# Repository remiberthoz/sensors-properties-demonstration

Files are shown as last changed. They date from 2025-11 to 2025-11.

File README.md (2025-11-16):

# Simulated absorbance sensors

This program simulates a series of light intensity sensors based on a single
physical sensor. It is designed primarily for educational purposes to teach
biology or chemistry students about sensor properties. Simulated sensors have
different properties (linearity, sensitivity, range, response time, noise).
The program visualizes the behavior of these simulated sensors in real-time,
allowing for a hands-on, inexpensive way to discover these concepts.

## Problems to fix / todo list...

- The calibration procedure is not OK, it should somehow take the value of
  MAX_A into account ; and likely the complete scaling (with to_byte).

- Try to output sensor values on DAC such that the students can work on an
  oscilloscope. Check if the DAC communication rate is good enough to
  simulate real analog.

- Program Arduino IO to read jumper status, and potentially allow students to
  change easily configuration.

## TECHNICAL REQUIREMENTS

### Hardware

The program is designed to run on an Arduino Uno board (or compatible) fitted
whith a companion shield that holds a light source, a light sensor, and a
sample holder for spectrophotometry cuvettes.

The light source and the sensor are positioned approximately 1 cm apart,
separated by the cuvette holder, which is used to adjust light intensities on
the sensor.

Refer to the schematic for connections and for part numbers that I used (also
see below). The cuvette holder was 3d printed, the 3d model is available.

shield_schematic

shield_layout

shield_cuvette_holder

#### Details on parts and wavelength choices

I decided to work with infrared light (935 +/- 25) nm to limit interference
from modern indoor lighting sources. I used a IR LED, OP140D with a 470R
resitor ; and a wavelength-matched OP550A IR NPN phototransitor kept in
linear regime using a 1k resistor on the emitter side.

Samples absorbing in infrared can easily be prepared with aqueous solutions
of copper sulfate. To avoid spills in the electronic lab, I mixed solutions
of copper sulfate with a preparation of 1 % agarose. It gelifies and stays in
the cuvettes.

Hydrated copper sulfate and agarose gel both absorb at 935 nm. The absorbance
of these prepared samples can be measured with a reference spectrophotometer.

### Software

This Arduino program works in tandem with a companion python program, which
runs on a computer to:

- Read data from the Arduino, through serial communication.
- Display a live graph of the sensors readings.

## Objective

This setup aims to teach students about sensor properties such as:

- Linearity
- Sensitivity
- Range (low and high saturations)
- Response time
- Noise

Students will visualize the response of several simulated sensors in
real-time. These sensors outputs are derived from the output of the physical
sensor, giving a sense of reality to the simulation (simulated sensors will
respond to change of absorbance standards, ambient light, light path
obstruction, ...).

This exercise allows students to explore how different sensors react to the
same physical change, producing different electrical outputs. Students can
create output-input graphs, measure response time, and compare sensors.

Instructors can adjust the sensors properties by change in code, rather than
by buying and mounting various sensors.

## Simulated sensors are *absorbance sensors*

In the context of biology and chemistry courses, students are typically
introduced to the concept of absorbance, often via spectrophotometry. Since
this concept is well known, and thus more intuitive than light intensity,
the sensors outputs a quantity linked to absorbance rather than light 
intensities (even though it really measures light intensities). This makes
it similar to how spectrophotometers usually work.

## Calibration

The setup can be calibrated by the instructors using samples of known
absorbance. Adjustements in the code can be made such that the Arduino
program can determine true absorbance internally, before deriving the output
values of simulated sensors.

Indeed, the sensor used on the Arduino shield is not necessarely linear
against light intensity itself.

## Prerequisites for students

Before using this system, students should:

- Understand the concept of absorbance as a property of a sample.
- Know that electronic sensors measure an electrical quantity (e.g., voltage,
  current), which is then mapped to physical parameters like absorbance.

These two facts explain why the output values are all different for a single
sample.

Students do not need to know that there is only one physical sensor in the
system. The setup can be presented as if multiple sensors are being used,
each with different response characteristics.

## Students focus on sensor characteristics

The main teaching goal is for students to understand how different sensors
behave, not how absorbance relates to light intensity. The system abstracts
this relationship by presenting data as voltage outputs (mapped to real
absorbance values via calibration). Students can focus on sensor
characteristics. This knowledge can later be transferred to any type of
sensor.

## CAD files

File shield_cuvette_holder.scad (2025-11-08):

$fn = 360 ;
margin = 0.01;
beam_height = 8.5;
redBeam_height = 15;

module smd0805(x, y, a=0) {
    smd0805_l = 3.7;
    smd0805_w = 1.9;
    smd0805_h = 1.0;
    translate([x, y, 0]) rotate([0, 0, a]) translate([-smd0805_l/2, -smd0805_w/2, -margin]) cube([smd0805_l, smd0805_w, smd0805_h+margin]);
}

module sideViewer(x, y, a=0) {
    sideViewer_l = 5.12;
    sideViewer_w = 2.30;
    sideViewer_h = 5.72;
    lense_d = 1.22;
    lense_dh = 1.22;
    
    beam_length = 10;
    beam_d2 = 2 * beam_length * tan(30);
    
    sideViewer_pitch = 2.54;
    sideViewer_legDim = 0.8;
    sideViewer_legLength = 12.70;
    
    translate([x, y, 0]) rotate([0, 0, a]) translate([0, 0, -(sideViewer_h-lense_dh-lense_d/2)+beam_height]) translate([-sideViewer_legDim/2, -sideViewer_legDim/2, 0]) {
        translate([0, 0, -sideViewer_legLength]) {
            translate([0, 0, 0])                cube([sideViewer_legDim, sideViewer_legDim, sideViewer_legLength+margin]);  // pin 1
            translate([sideViewer_pitch, 0, 0]) cube([sideViewer_legDim, sideViewer_legDim, sideViewer_legLength+margin]);  // pin 2
        };
        translate([-sideViewer_l/2+sideViewer_pitch/2+sideViewer_legDim/2, -sideViewer_w/2+sideViewer_legDim/2, 0]) cube([sideViewer_l, sideViewer_w+beam_length, sideViewer_h+10]);  // head
        translate([sideViewer_pitch/2+sideViewer_legDim/2, sideViewer_w/2+sideViewer_legDim/2, sideViewer_h-lense_dh-lense_d/2]) rotate([-90, 0, 0]) cylinder(h=beam_length, d1=lense_d, d2=beam_d2); // beam
    }
}

module bendT1(x, y, bentHeight=0, bentLength=4) {
    legDim = 0.8;
    legLen = 27;
    legPitch = 2.45;
    
    hLegLen = bentLength < 0 ? legLen-bentHeight : bentLength;
    vLegLen = legLen - hLegLen;
    
    translate([x-legPitch/2, y-hLegLen, bentHeight]) {
        translate([-4.0/2, -(3.0+4.0+hLegLen)/2, -4.0/2]) cube([4.0, 3.0+4.0+hLegLen, 4.0]);
        rotate([90, 0, 0]) {
            translate([-legDim/2+legPitch/2, -legDim/2, -hLegLen]) cube([legDim, legDim, hLegLen]);
            translate([-legDim/2-legPitch/2, -legDim/2, -hLegLen]) cube([legDim, legDim, hLegLen]);
        }
        translate([-legDim/2+legPitch/2, -legDim/2+hLegLen, -vLegLen]) cube([legDim, legDim, vLegLen]);
        translate([-legDim/2-legPitch/2, -legDim/2+hLegLen, -vLegLen]) cube([legDim, legDim, vLegLen]);
        
        rotate([90, 0, 0]) {
            cylinder(h=4.45-3.0/2, d1=3.1, d2=3.0);
            translate([0, 0, 4.45-3.0/2]) sphere(d=3.0);
            cylinder(h=1, d=3.2);
        }
    }
}

module m2(x, y, h=10) {
    m2_diameter = 2.2;
    m2_diameter_head = 6;
    translate([x, y, -h/4]) cylinder(h=h, r=m2_diameter/2);
    translate([x, y, h/4]) cylinder(h=100, r=m2_diameter_head/2);
}

module cuveHole(x, y, l=100, h=100, window_dh=0, a=0) {
    cuve_dim = 12.8; // with tolerance (12.5+/-0.2 and 0.1 extra margin)
    window_width = 6;
    window_height = 6;
    translate([x, y, 0]) {
        translate([-cuve_dim/2, -cuve_dim/2, -margin]) cube([cuve_dim, cuve_dim, window_dh+h+margin]);
        //translate([-window_width/2, -l/2, window_dh-margin]) cube([window_width, l, h+margin]);
        translate([-cuve_dim/2, -cuve_dim/2, 0]) cube([cuve_dim, cuve_dim, 45]);
    }
}

difference() {
    cube([22.86, 33.02, 15]);
    translate([-margin, -margin, -margin]) cube([13.335+margin, 2.54+margin, 3+margin]);
    
    sideViewer( 8.89,  5.08);  // Q1
    sideViewer(11.43, 25.40, a=180);  // D1
    

    smd0805( 8.89, 34.02, a=90);  // R3
    smd0805( 6.35, 34.02, a=90);  // R2
    smd0805(10.43,  2.54);  // R1

    m2(19.05,  4.445);
    m2( 3.81, 27.94);
    
    cuveHole(10.16, 15.24, l=25, h=15);
    bendT1(11.43, 30.48, redBeam_height);
}

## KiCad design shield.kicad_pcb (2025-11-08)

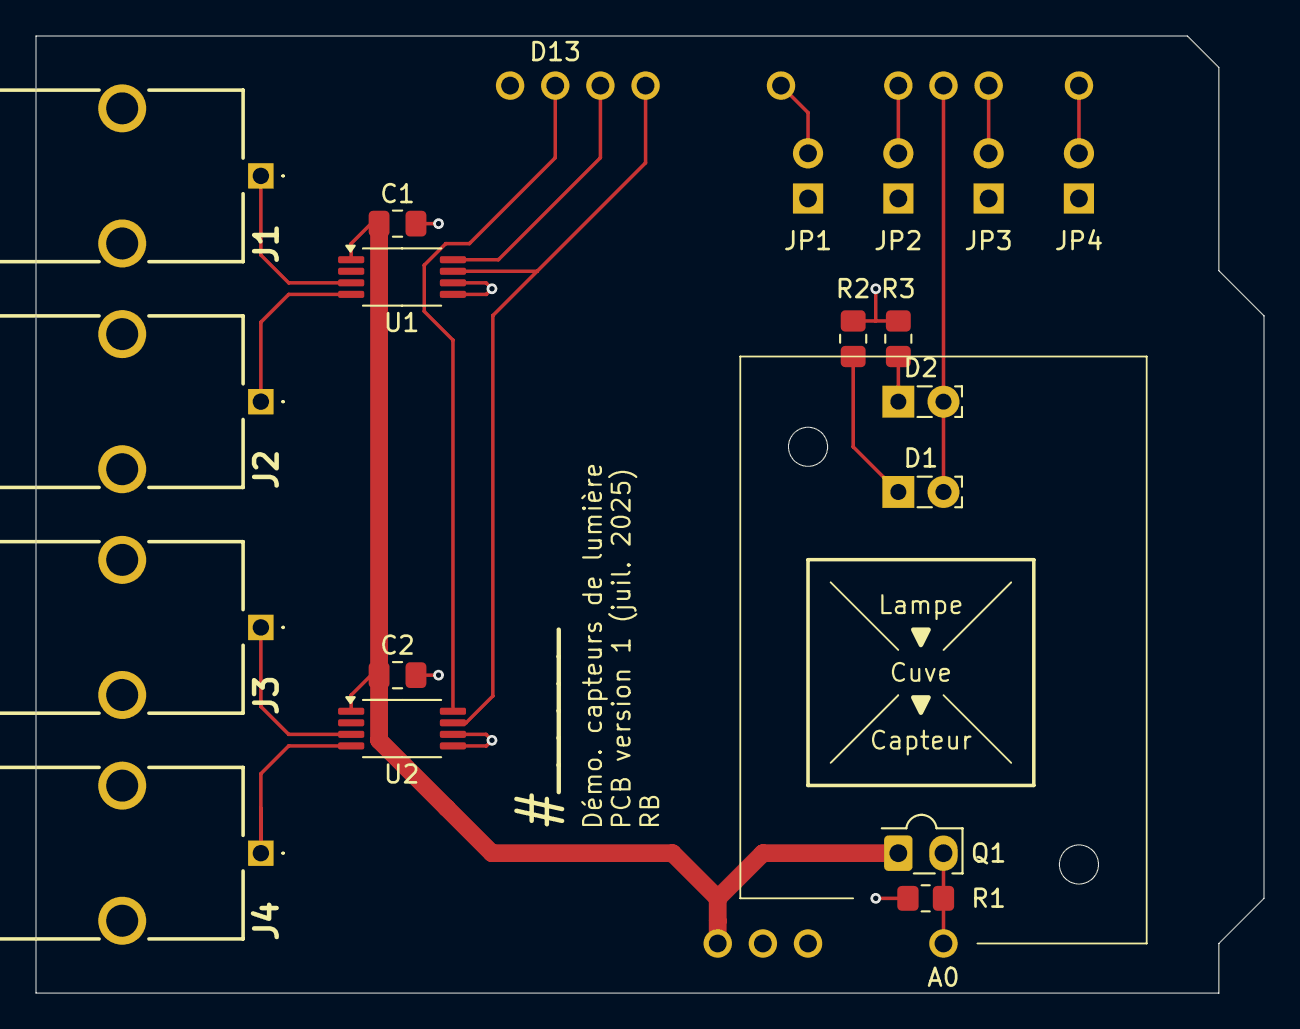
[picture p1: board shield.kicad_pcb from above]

Board: 2 copper layers, 69.1 x 53.8 mm, 19 parts (1 on the bottom side), 17 nets.

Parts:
A1: Arduino_UNO_R3
C1, C2: C; C_0805_2012Metric_Pad1.18x1.45mm_HandSolder
D1: OP140D (IR); LED_SideEmitter_Rectangular_W4.5mm_H1.6mm
D2: LTL-307P (Red); LED_SideEmitter_Rectangular_W4.5mm_H1.6mm
J1, J2, J3, J4: Conn_Coaxial; 731713150
JP1, JP2, JP3, JP4: Jumper_2_Open; PinHeader_1x02_P2.54mm_Vertical
Q1: OP550A (IR); Osram_LPT80A
R1: 10k; R_0805_2012Metric_Pad1.20x1.40mm_HandSolder
R2, R3: 220 min; R_0805_2012Metric_Pad1.20x1.40mm_HandSolder
U1, U2: TSSOP-8_4.4x3mm_P0.65mm

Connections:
/ANALOG1: J1.1 (In), U1.3 (VOUT0)
/ANALOG2: J2.1 (In), U1.4 (VOUT1)
/ANALOG3: J3.1 (In), U2.3 (VOUT0)
/ANALOG4: J4.1 (In), U2.4 (VOUT1)
/ANALOG_SENSE: A1.9 (A0), Q1.2 (E), R1.1
/LED_CONTROL: A1.20 (D5), D1.2 (A), D2.2 (A)
/SCL: A1.26 (D11), U1.7 (SCL), U2.7 (SCL)
/SDA1: A1.27 (D12), U1.8 (SDA)
/SDA2: A1.28 (D13), U2.8 (SDA)
GND: A1.6 (GND), A1.7 (GND), A1.29 (GND), C1.2, C2.2, J1.2 (Ext), J2.2 (Ext), J3.2 (Ext), J4.2 (Ext), JP1.1 (A), JP2.1 (A), JP3.1 (A), JP4.1 (A), R1.2, R2.2, R3.2, U1.5 (VSS), U1.6 (LAT0/HVC), U2.5 (VSS), U2.6 (LAT0/HVC)
unnamed: A1.17 (D2), JP4.2 (B)
unnamed: A1.19 (D4), JP3.2 (B)
unnamed: A1.21 (D6), JP2.2 (B)
unnamed: A1.23 (D8), JP1.2 (B)
unnamed: D1.1 (K), R2.1
unnamed: D2.1 (K), R3.1
VCC: A1.5 (+5V), C1.1, C2.1, Q1.1 (C), U1.1 (VDD), U2.1 (VDD)

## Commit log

2025-11-09 Add schematic and layout images to README
    Added images of the schematic, layout, and cuvette holder to the README.
2025-11-09 feat: accumulate reads while waiting, then average
    Instead of waiting the next tick doing nothing, we can read sensor
    values and average the results from the whole sampling period.
    This really makes a "sampling period" instead of a "sampling
    interval". It will greately reduce noise on the physical sensor,
    but also lower the response time of the internal "calibrated"
    sensor from that of the physical sensor (few µs) to that of the
    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
2025-11-16 local: update calibration data for my own boards
2025-11-19 doc: indicate new todo list item (Baud rate adjustment)
    Baud rate of 115200 seems too high to work reliably with USB cables in the classroom.
2025-11-25 feat: lower Baud rate, make TX robust for poor USB
    Arduino transmits 1 byte per sensor + 1 byte. With a high estimate
    of 7 sensors (8 bytes to transmit), it takes 6 ms to transmit data
    at a baud rate of 9600 bit/s. This leaves enough time for the
    remainings of the 25 ms period, both on Arduino and on PC, to
    measure and to plot.
